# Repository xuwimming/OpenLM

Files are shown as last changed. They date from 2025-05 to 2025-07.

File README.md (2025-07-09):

---

# *OpenLM: An Open-Source Pixel Super-Resolution Platform for Lens-Free Microscopy*

OpenLM is a fully open-source, 3D-printed lens-free microscopy platform that integrates affordable, commercially available components with a pixel super-resolution algorithm. It features an intuitive graphical user interface and supports both **Raspberry Pi OS** and **Windows OS** for seamless camera control, real-time preview, image acquisition, and image processing — all without requiring prior experience in lens-free imaging.

---

## 🔧 Features

* Affordable, accessible hardware (Raspberry Pi, LED array, filters, and Pi Camera)
* Pixel super-resolution algorithm for enhanced image quality
* User-friendly GUI applications for both Raspberry Pi and Windows
* Fully open-source software paired with 3D-printable hardware designs

---

## 📋 Material List

| Component                      | Quantity   | Price    |
|-------------------------------|------------|----------|
| Raspberry Pi Camera Module 2   | 1 unit     | $14.99   |
| Thorlab 532 nm Filter          | 1 unit     | $164.67  |
| Adafruit DotStar 8x8 LED array | 1 unit     | $24.95   |
| 6mm Neodymium Magnets       | 4 units    | $0.08    |
| Raspberry Pi 4B                | 1 unit     | $75.00   |
| PLA for 3D Printed Casing     | 187 g      | $4.68    |
| **Total**                     |            | **$284.37** |

---

## 🛠️ OpenLM Assembly Workflow

<p align="center">
  Workflow
</p>

A–B. Insert four neodymium magnets into the Raspberry Pi cover and the platform holder — two in each part.

C. Connect the LED array to the Raspberry Pi.

D. Insert the optical filter into the filter tray on the platform.

E. Mount the LED array and Raspberry Pi onto the platform. The small alignment pegs on the platform fit into corresponding holes on the LED array and Raspberry Pi 4B, securing their positions.

F. Attach the camera module to the platform. Alignment pegs will hold the module in place. Route the camera cable through the designated slot and connect it to the camera port on the Raspberry Pi.

G. Cover the illumination module and Raspberry Pi with their respective covers to isolate and protect the illumination system.

---

## 🧰 Removing the Lens from Raspberry Pi Camera 2

<p align="center">
  Remove Lens
</p>

The red arrows indicate the glue line between the Raspberry Pi Camera 2’s CMOS sensor and lens unit. To remove the lens unit from the top of the CMOS, carefully cut along the glue line using a blade. Note that the lens unit has thin plastic walls, so extra caution is needed during removal to avoid damage.

---

## 📦 Installation (Dependencies)

Ensure Python and pip are installed, then run:

```bash
sudo pip install adafruit-circuitpython-dotstar
sudo pip install rawpy
sudo pip install scipy
sudo pip install flask_socketio
sudo pip install imageio
sudo pip install scikit-image
sudo pip install image_registration
```

---

## 🛠 Common Issues & Fixes

**Issue:**
`ValueError: numpy.dtype size changed, may indicate binary incompatibility. Expected 96 from C header, got 88 from PyObject`

**Solution:**
Install a compatible NumPy version:

```bash
sudo pip install numpy==1.26.4
```

---

**Issue:**
Permission denied when saving files

**Solution:**
Run the application with elevated privileges:

```bash
sudo python /path/to/OpenLM_RP.py
```

---

## 🔗 Mounting a Windows Shared Folder on Raspberry Pi

To access a Windows shared folder from your Raspberry Pi:

```bash
sudo apt install cifs-utils
mkdir ~/shared
sudo mount -t cifs //YourPCName/SharedFolder ~/shared -o username=YourWindowsUsername
```

---

## 🖥️ GUI Usage Instructions

---

### Raspberry Pi GUI

<p align="center">
  Raspberry Pi GUI
</p>

1. **Left Checkbox** – Enable analysis of the captured hologram on a connected desktop.
2. **Middle Checkbox** – Perform focusing directly on the Raspberry Pi. *(Note: Raspberry Pi 4B or above is recommended for reliable performance.)*
3. **Right Checkbox** – Enable **real-time pixel super-resolution (PSR)**.

   > Requires the **"Client"** checkbox to be selected. This increases processing time during image capture.

<p align="center">
  Optional Settings
</p>

4. **LED Array Preview** – The effective LEDs used during imaging are highlighted in red:

<p align="center">
  LED Array
</p>

5. **Current Time Display** – Shows the timestamp of the image currently displayed.

   > This is especially useful when PSR processing takes longer than the image capture interval.

<p align="center">
  Current Time Display
</p>

---

### 🖥️ Windows GUI

<p align="center">
  Windows GUI
</p>

1. **Connection Indicator** – When the connection to the Raspberry Pi is established successfully, the status indicator turns **green**.

   <p align="center">
     <table align="center" cellspacing="10" cellpadding="0" style="border:none;">
       <tr>
         <td>Disconnection Indicator</td>
         <td style="vertical-align: middle; font-size: 40px;">➡️</td>
         <td>Connection Indicator</td>
       </tr>
     </table>
     </p>

2. **Frames** – Specifies the number of frames the user wishes to process.

   <p align="center">
     Frame Setting
   </p>

---

### 🗂️ Save Image Folder Structure

**Single LR Hologram Capture**

Selected Folder

  └── Selected file name.jpg and .dng

**Single HR Hologram Capture**

Selected Folder

│  ├── 0.jpg and 0.dng

│  ├── 1.jpg and 1.dng

│  ├── ...

│  └── 63.jpg and 63.dng

**Time-Lapse Hologram Capture**

Selected Folder

│  ├── 0

│  │  ├── 28 jpg files

│  │  └── 28 dng files

│  ├── 1

│  │  ├── 28 jpg files

│  │  └── 28 dng files

│  ├── ...

│  ├── N    

│  │  ├── 28 jpg files

│  │  └── 28 dng files

---

### 📁 Additional Files

1. **`Shifting_Map_Generation.ipynb`** (located in the `Windows Application` folder)
   This notebook is used to generate a high-accuracy shifting map for high-resolution (HR) image reconstruction. While the main application can also generate a shifting map, we **highly recommend** using this notebook for more accurate results.
   
   🔹 *Note:* Each focusing object from a different depth requires its corresponding shifting map.

3. **Focal Plane Estimation**
   The same notebook also estimates the optimal focal plane of the target object. Updating the focus setting through the GUI based on this estimation can significantly improve the accuracy and speed of the reconstruction algorithm.

4. **Modify Focal Plane Start Value**
   Update the `z_start` value in the `OpenLMlib.py` file, inside the `imageReconstruction_unknownZ_loop` function.
   This value corresponds to the estimated focal plane of the low-resolution hologram and should be set based on the result from `Shifting_Map_Generation.ipynb`.

   <p align="center">
     Focal Plane GUI
   </p>

5. **`Post_Processing.ipynb`** (in the `Windows Application` folder)
   This notebook batch-processes all captured frames and compiles a time-lapse video.
   
   ⚠️ *Important:* If real-time processing is enabled, the application will continue running until all captured frames are processed. For back-to-back experiments, we recommend capturing all images first and then performing post-processing afterward using this notebook.

---

### 📚 Citation



---

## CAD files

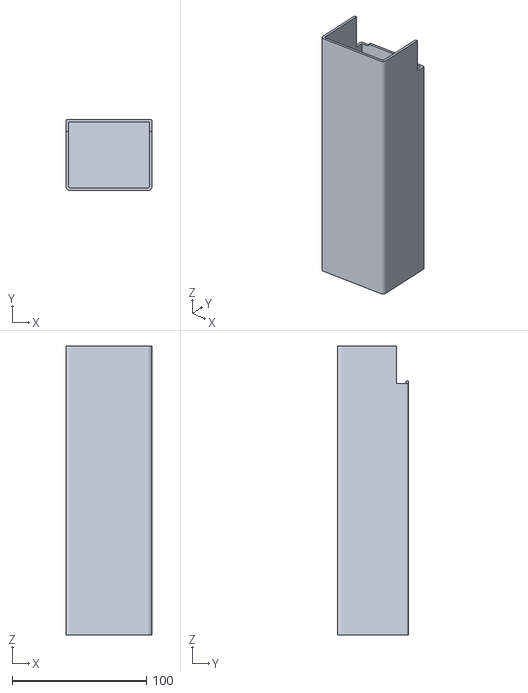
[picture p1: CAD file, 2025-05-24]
3D Printing Parts/Light Cover.STL
64.0 x 53.0 x 215.0

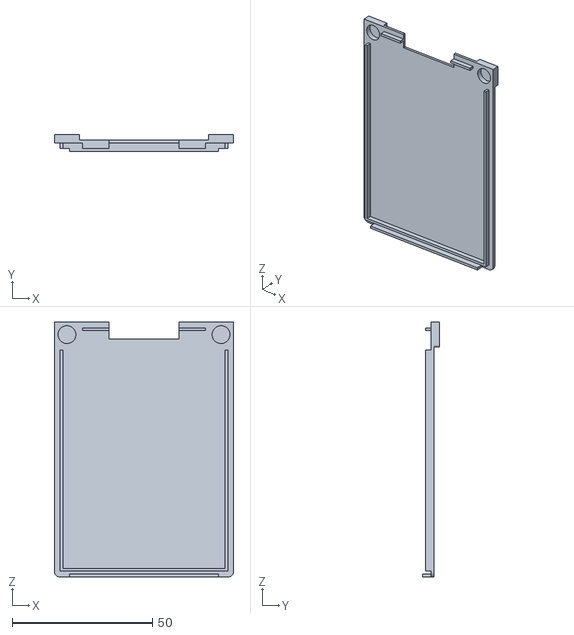
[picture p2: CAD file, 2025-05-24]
3D Printing Parts/Raspberry Pi Cover.STL
64.0 x 6.00 x 91.0

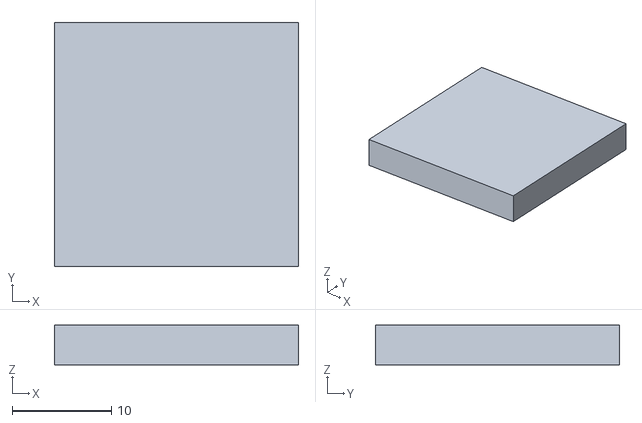
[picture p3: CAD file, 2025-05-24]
3D Printing Parts/Petri Dish Helper.STL
24.6 x 24.6 x 4.00

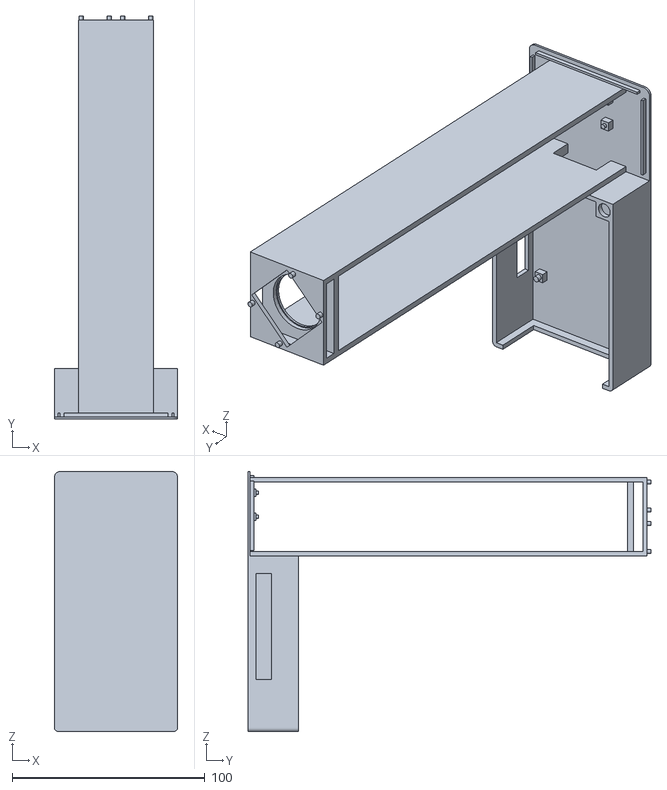
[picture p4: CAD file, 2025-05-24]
3D Printing Parts/Device Base.STL
64.0 x 209.0 x 135.0
